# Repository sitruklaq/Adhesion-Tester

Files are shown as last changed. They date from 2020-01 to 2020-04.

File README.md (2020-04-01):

# Hattonlab Adhesion-Tester

This is the repository and working instructions for the linear-force tester in the HATTONLAB at the University of Toronto. This device is designed to test various forces under linear displacement. For example: Adhesion, Friction, or Tensile Strength. The device is built upon a modular breadboard which means it can be modified to run many different tests.

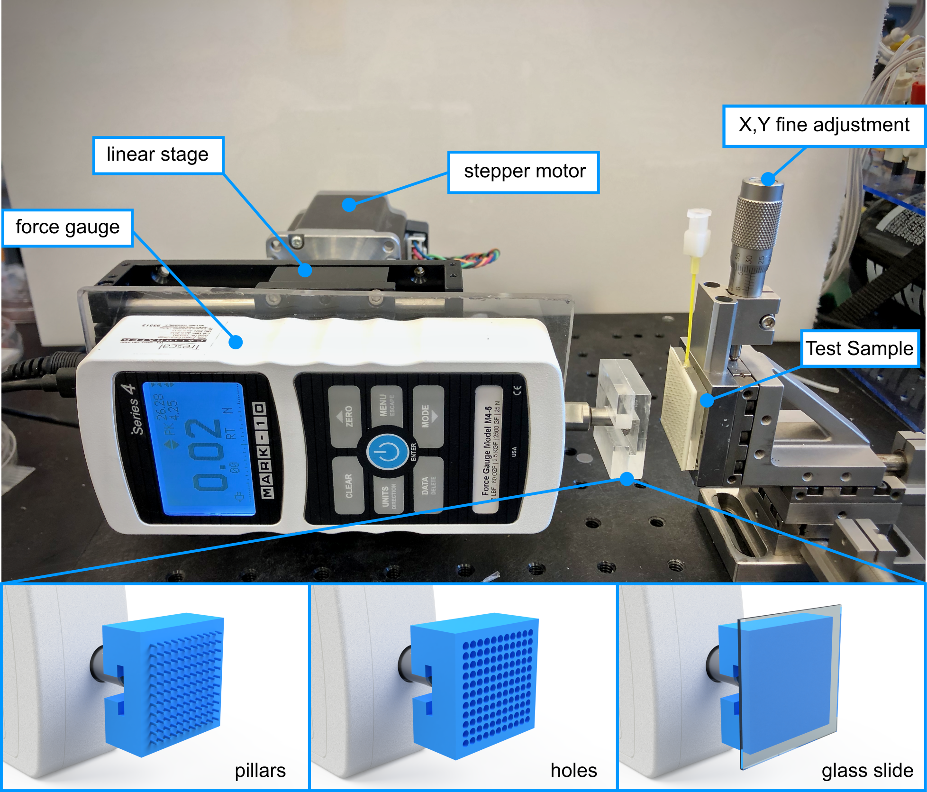
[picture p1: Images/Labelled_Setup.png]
setup


### Force Capacity, Resolution, and Accuracy

The Mark-10 M4 25N has a working range of +-25N with a resolution of  0.01N and accurate to +-0.2% of 25N.

# Construction & Components

Physical Base:
- Base breadboard (Newport Aluminum 1ftx1ft Breadboard)
- Linear Rail and aluminum plate (From an old printer)
- X,Y fine adjustment & Sample holder (Newport 461)
- Force Gauge to Linear Rail coupling plate (custom milled)
- Stepper Motor to Linear Rail coupling (McMaster Carr ???)

Electrical Components:
- Stepper motor/Motor controller (Oriental Motor)
- Force gauge and Accessory Kit (Mark-10 M4 25N)
- USB to RS-485 converter

Attachment Tips: 
The force gauge included the following attachment tips:

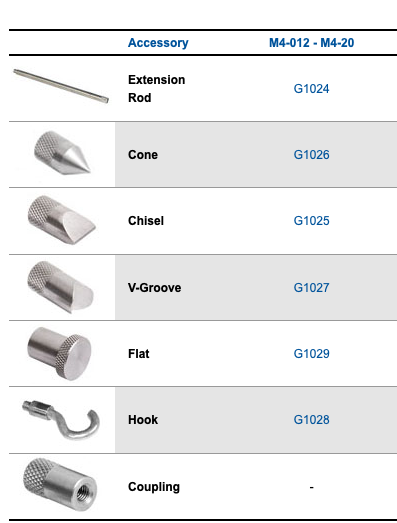
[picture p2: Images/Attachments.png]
image of included attachments


A custom milled attachment piece has also been created to attach onto the 'flat accessory to generate a larger surface area (1.2"x1.2").

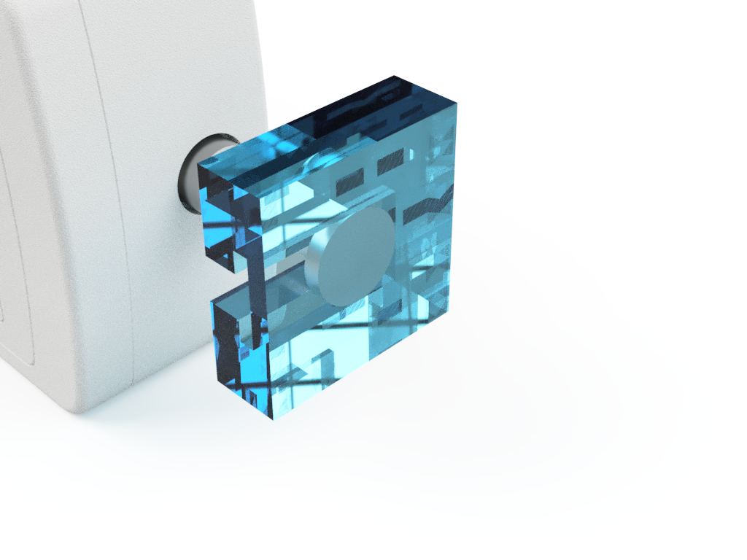
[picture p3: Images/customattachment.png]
image of custom attachment


### Calibration

A correlation between motor steps (pulses) and distance travelled was used to calibrate the machine:

Using the following controller configuration:

Any change to these settings will require a recalibration. 

At current: 1mm = 566pulses

Example: 
```
Real Displacement and Rate: 50mm at 2mm/s
Pulses: 28350pulse at 1132pulse/s
```

#### Calibration Steps:

1. Open the Motion Creator App. 
2. Measure the distance between two points on the linear rail.
3. Create a movement operation for a known number of 'steps/pulses' (e.g. 1000). 
4. Measure the new distance between the two points. Do this for an adequant number of times.
5. Plot a Position vs Pulse chart and extract the slope. The slope represents the number of pulses required to move 1mm.

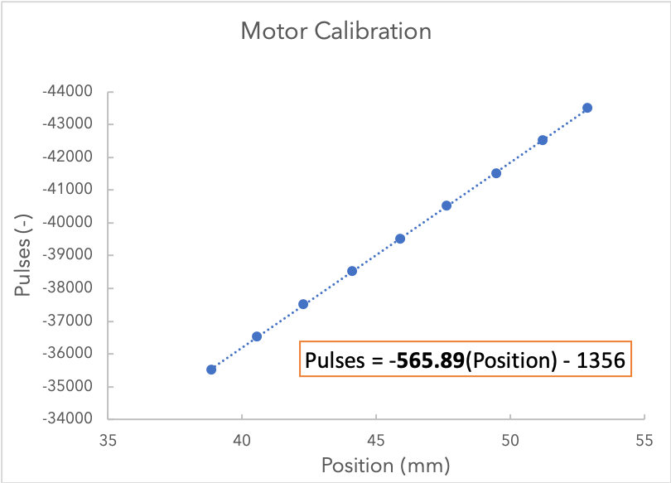
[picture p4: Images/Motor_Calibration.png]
Motor_Calibration


# Operation Modes

There are two methods of control:

1. **Manual** (basic): Motion and force are indepentely controlled through proprietary graphical software Why manual control?

   - It is easier to get started
   - Requires no knowledge of scripting or MATLAB

2. **Script** (advanced): MATLAB scripting that allows for automated, precise, and advanced test parameters (e.g. Force limiting) 

   Why script control?

   - **Linked Data**: Position and Load start/stop recording at equal times and record at equal rates
   - **Load Control**: This allows you to reach precise preloads, and have motions based on the load such as stopping at failure (0 load) or reaching precise preloads.
   - **Autonomous Testing**: single button to start testing can perform multiple tests, save data, and interact with tertiary devices such as pneumatics

## 1. Manual Control
Manual control uses proprietary software to separately control the force gauge and stepper motor. 

### Software Required

#### Stepper Motor Software: CRK Motion Creator

This allows you to change the gearing, jog the motor, and write scripts for motion. [Download Link](https://www.orientalmotor.com/downloads/software.html#)

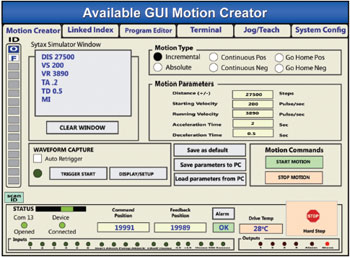
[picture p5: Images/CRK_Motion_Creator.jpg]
CRK UI


#### Force Gauge Software: MESUR Lite

This allows you to record force gauge reading and export to Excel. [Download Link](https://www.mark-10.com/instruments/software/mesurlite.html)

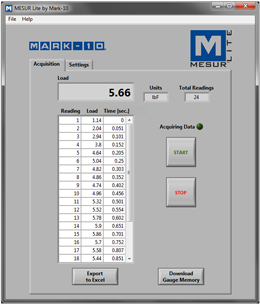
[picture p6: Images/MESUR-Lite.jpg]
MESUR UI


### Running a Manual Test

1. Open Both MESUR Lite and CRK Motion Creator
2. Enter desired motion commands such as velocity, acceleration and distance using the calibration above
3. Jog the stepper motor to the starting postion
4. Start recording in MESUR (make sure record rate and max data points are set in Settings)
5. Press start on the motion commands
6. Allow test to run
7. Stop recording on MESUR and export data to Excel

## 2. Script Control

The scripting program used in this work is MATLAB.

### Running a Scripted Test

1. Write a script using the commands and examples below:
2. Jog the motor into place using CRK Motion Creator
3. input start position and any other variables into script
4. Run the script

# Writing Commands

#### Connecting the Instruments

The first step is to connect the instruments through serial connection.

This is a Matlab function that connects the force gauge and stepper motor.

```matlab
function [force_gauge, step_motor] = connect_instruments()
%connect_instruments Connects Mark-10 force gauge and step motor

    % These serial ports should be changed depending on the computer

    % Connect Force Gauge
    force_gauge = serial('COM6');
    force_gauge.Baudrate = 115200;
    fopen(force_gauge);

    % Connect Step Motor
    step_motor = serial('COM7');
    fopen(step_motor);
    step_motor.RecordDetail ='Verbose';
    record(step_motor)
end
```

## Stepper Motor Commands

Once the instruments are connected, they can receive and send information through writing through the Serial Port.

The full list of commands can be found in Section 13 Command List from the Controller Operating Manual.

However, these are some of the most utilized commands:

| Command | Function                                                     |
| ------- | ------------------------------------------------------------ |
| TA / TD | Acceleration and deceleration time, respectively             |
| DIS     | Distance to move in pulses. Define this before the MI command |
| VS / VR | Starting Velocity and running velocity, respectively         |
| MA      | Move Absolute. Moves to                                      |
| MI      | Move Incrementally (start motion) and continue until distance has been achieved |
| PSTOP   | Panic stop: Hard stop, system state after stop is defined by ALMACT |
| HSTOP   | Hard stop: stop as quickly as possible                       |
| SSTOP   | Soft stop: controlled deceleration over time                 |

The code does not currently use the following commands but they might be useful

| Command | Function               |
| ------- | ---------------------- |
| MEN     | Wait for Motion to end |
| WAIT    | Time delay (seconds)   |

**IMPORTANT**:The absolute position is reset to 0 if unplugged. Therefore,  if using the MA command, it is **EXTREMELY** important to check the starting position before starting a MATLAB script. In future versions,  'home seeking' would solve this issue. 

### Example: 

Move the force gauge back 15mm at 2mm/s with minimal ramp up time. The original pulse position is 117000.

Data to the step motor is expected in the following format: 

```
COMMAND VALUE
example: VS 1000
```

Distance Method (dont use if possible):

```matlab
fprintf(step_motor, 'TA 0.1') % ramp up time
fprintf(step_motor, 'TD 0.1') % ramp down time
fprintf(step_motor, 'VS 1132'); % starting velocity 2mm/s * 566pulse/mm = 1132
fprintf(step_motor, 'VR 1132'); % running velocity
fprintf(step_motor, 'DIS -120000'); % distance to travel -15mm * 566pulse/mm = 8490
fprintf(step_motor, 'MI'); % start motion
```

Abosolute Movement Method (preffered):

```matlab
fprintf(step_motor, 'TA 0.1') % ramp up time
fprintf(step_motor, 'TD 0.1') % ramp down time
fprintf(step_motor, 'VS 1132'); % starting velocity 2mm/s * 566pulse/mm = 1132
fprintf(step_motor, 'VR 1132'); % running velocity
fprintf(step_motor, 'MA &s\n',num2str(117000-8490)); % distance to travel -15mm * 566pulse/mm = 8490.. 

```

*During early testing, it was found that the stepper motor would sometimes miss move commands. This can be hazerdous to the machine if the motor moves bi-directionally. For example, the force gauge may ram into the substrate and overload if a 'move back' command is missed, leading to two sequental 'move forward commands'. Therefore, it is recommended to use position commands (MA) instead of distance commands (MI).*

## Force Gauge Commands

Once connected, the force gauge will return the current load when asked.

Sample Code:

```matlab
fprintf(force_gauge,char('?',13,10));
resp = fscanf(force_gauge);
```

This snippet writes a serial command to the force gauge, asking for the current char. It then reads the reponse and stores the force as 'resp'.

## Sample Test

This is a simple tensile test that retracts the force gauge at a constant rate for a determined distance. Examples in the code section demonstrate more complex functions such as additional states (approaching, dwelling, and retracting), and force control (preloading, test termination at 0 force etc..).

```matlab
% This is a basic tensile test
%% CONNECT INSTRUMENTS
delete(instrfind)
clear;

force_gauge = serial ('COM6');
force_gauge.Baudrate = 115200;
fopen(force_gauge);

step_motor = serial('COM7');
fopen(step_motor);
step_motor.RecordDetail = 'Verbose';
record(step_motor)

%% USER INPUT VARIABLES
alarm_force = 25; % Force (N) to trigger the alarm
approach_velocity = 1 % enter approach velocity in mm/s
retract_velocity = 2 % enter retract velocity in mm/s
start_position = 115000 % IMPORTANT start position in pulses
distance = 15 % distance to move in mm
reading delay = 0.25; % time between collected data points.. 0.25 = 4 reading/s
%% INITIZIALIZATION
retract_velocity_pulse = retract_velocity*566;
retract_distance_pulse = distance*566;
paused = false;
pause_time = 0;
pause_target = 0;
retract = true;
test_done = false;

data = zeros (10,1); %Create the data matrix for storing force
count = 1;

fprintf(step_motor, 'TA 0.1'); %sets ramp times to as quick as possible
fprintf(step_motor, 'TD 0.1');

%% TEST LOOP
while(running_test)

% Force Recording
fprintf(force_gauge,char('?',13,10));
resp = fscanf(force_gauge);
current_force = str2double(resp(1:end-3));
data(count) = current force;
count = count+1;

% Alarms that quit the program to save the force gauge from overloading
if current_force > alarm_force 
test_done=true
fprintf(step_motor,'ABORT');
pause (0.01);
fprintf(step_motor, 'DIS -20000');
fprintf(step_motor, 'MI');
disp ('ERROR: FORCE OVERLOAD. RETRACTING AND QUITTING')
pause (20);
delete(instrfind)
end
if current_force<(-1*alarm_force)
test_done=true
fprintf(step_motor,'ABORT');
pause(0.01);
fprintf(step_motor, 'DIS 1000');
fprintf(step_motor, 'MI');
disp ('ERROR: NEGATIVE FORCE OVERLOAD. PUSHING AND QUITTING')
delete(instrfind);
end
%-- end of alarm section

% Test states. This example includes only a retract state. Add additional states such as approach and dwell for more complex testing

if ~paused && retract
disp ('Pulling Surfaces Apart')
pause (0.01);
fprintf(step_motor, 'VS %s\n', num2str(retract_velocity_pulse));
pause (0.01);
fprintf(step_motor, 'VR %s\n', num2str(retract_velocity_pulse));
pause (0.01);
fprintf(step_motor, 'MA %s\n', num2str(start_position - retract_distance_pulse ) )

pause_target = (4+ double(distance)/double(retract_velocity))
retract=false;
paused=true;
test_done=true;

elseif ~paused && test_done
running_test = false;

elseif paused
pause_time = pause_time+1;
if pause_time >=pause target
paused=false;
pause_time=0;
end
end
pause(reading_delay);
end
%% POST TEST DATA WRITING
writematrix(data, ['data/',datestr(now,'mm-dd-yyyy-HHMM'), 'testname.csv')];
disp('TEST DONE')
```

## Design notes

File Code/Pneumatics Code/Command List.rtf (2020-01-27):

Command List

VO Opens or closes output valves

The first numeric input defines which out valve you are addressing. There are currently 8 valves which can be addressed by 0-7.

The second numeric input defines state. 1= ON, 0=OFF.

<VO, 1 , 1> turns on the second output valve.

VI Opens of closes the input valves

This works exactly like VO except there are only 3 input valves (0,1,2).

0-Negative
1-Exhaust
2,Positive

<VI, 0, 0> Turns off the negative input valve

PSP Assigns a Setpoint pressure value for the positive chamber

<PSP, 25> assigns a Setpoint of +25KPa

NSP Assigns as Setpoint pressure value for the negative chamber

<NSP, -25> assigns a Setpoint of -25KPa

STATE Reports the state of every component through the serial port

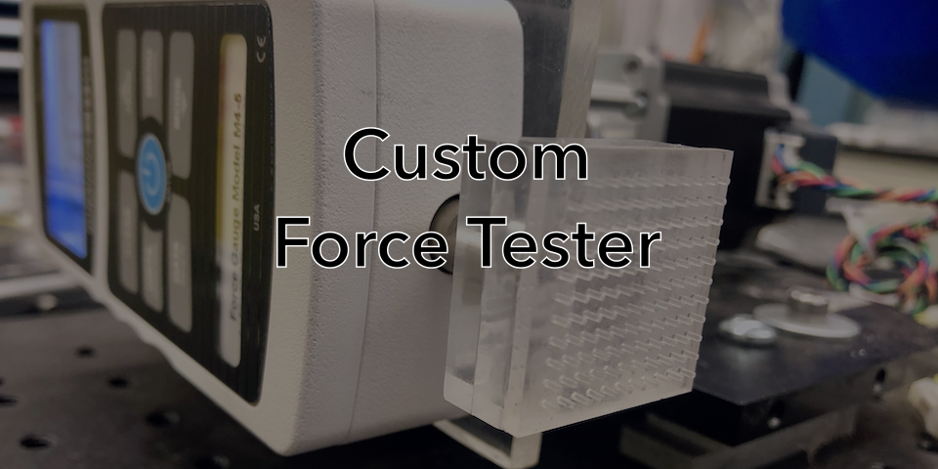
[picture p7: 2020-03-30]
Images/rect4821.png

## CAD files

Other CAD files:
CAD Files/B547 MOTOR CONROLLER.dwg
CAD Files/Adhesion Tester Rotation Plate.f3d

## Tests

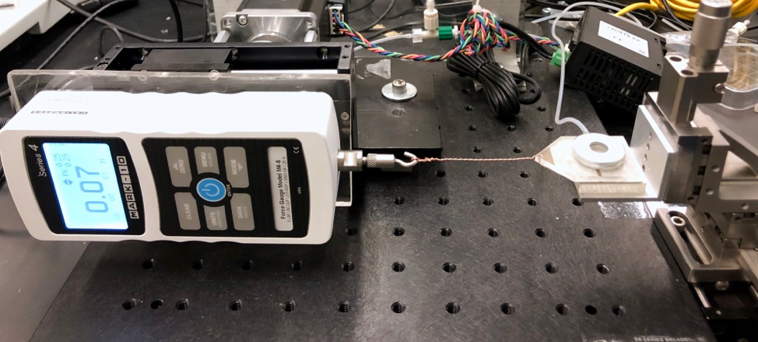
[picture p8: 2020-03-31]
Images/Additional Setup Images/adhesion_tester_friction.png

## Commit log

2020-01-27 create new repo
    [Adhesion Tester Rotation Plate.f3d]
2020-03-31 Update Readme with sample test
    [10N - pillar intensity.csv, 3.5mm sample - 01N preload.csv, 3.5mm sample - 02.5N preload.csv, 3.5mm sample - 04N preload.csv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]
